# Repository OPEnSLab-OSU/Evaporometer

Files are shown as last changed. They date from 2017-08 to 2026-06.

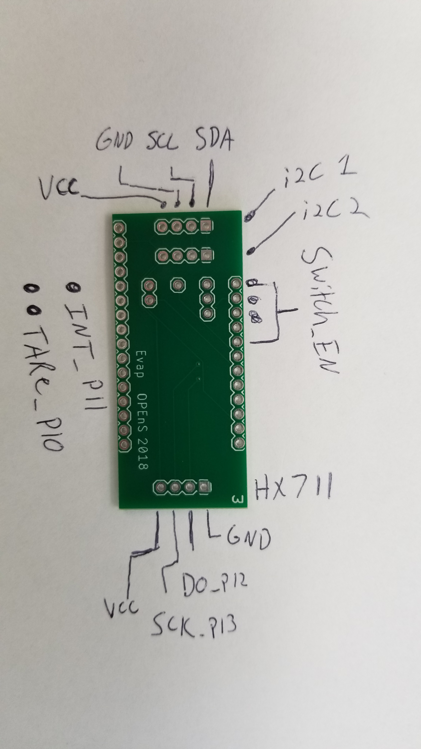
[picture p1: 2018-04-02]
PCB/20180402_102329.jpg

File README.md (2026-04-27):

# OPEnS Lab Evaporometer

Here are documented all of the files and links regarding the evapor0meter. This includes all of code and CAD files to create and program the entire system. It also includes a link to the lastest data collected in the field. 

For an overview of the project view the [Evaporometer Wiki](https://github.com/OPEnSLab-OSU/OPEnS-Lab-Home/wiki/Evaporometer)

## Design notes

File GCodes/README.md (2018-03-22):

This folder contains some important GCodes genereated for the Fusion3 F-400 printer using Simplify3D slicer program.

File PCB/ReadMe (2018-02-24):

Place to store archived EagleCAD PCB projects. Files shoudl have last data modified and version number in the name.

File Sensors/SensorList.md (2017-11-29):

These are the sensors that are on the Evaporimeter: 

[SHT31-D](https://www.adafruit.com/product/2857)  

[Load Cell](https://www.amazon.com/uxcell-Electronic-Balance-Weighing-Sensor/dp/B006W2IDUO/ref=sr_1_1?s=home-garden&rps=1&ie=UTF8&qid=1494279830&sr=1-1&keywords=load+sensor+2kg&refinements=p_85:2470955011)

[Light Sensor](https://www.adafruit.com/product/1980)

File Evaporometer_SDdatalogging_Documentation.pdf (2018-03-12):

Evaporometer PCB Pin Configuration

Feather 32u4 | P13 | P12 | P11 | P10 | P7 | P6 | P5 | SCL | SDA
Connection | HX711_ SCK (load cell) | HX711 _D0 (load cell) | DS3231_S WQ/INT (RTC) | Tare_ button | [reserved for battery input read voltage] | [open] | [open] | All SCL signals | All SDA signals

MicroSD card breakout board + (External data storage)
- Takes both 3V and 5V power source, has an onboard voltage regulator to shift 5V down to 3V.
- Keep wires short, avoid using resistor dividers for the 3.3V logic lines.
- Interface: SPI Mode “lower speed”, use this, requires four pins
- Format using FAT16 or FAT32 filesystem
- Require a lot of data transfer, best performance when connected up to the hardware SPI pins on a microcontroller.
- Use the Arduino IDE's SD library which supports FAT and FAT32 SD cards

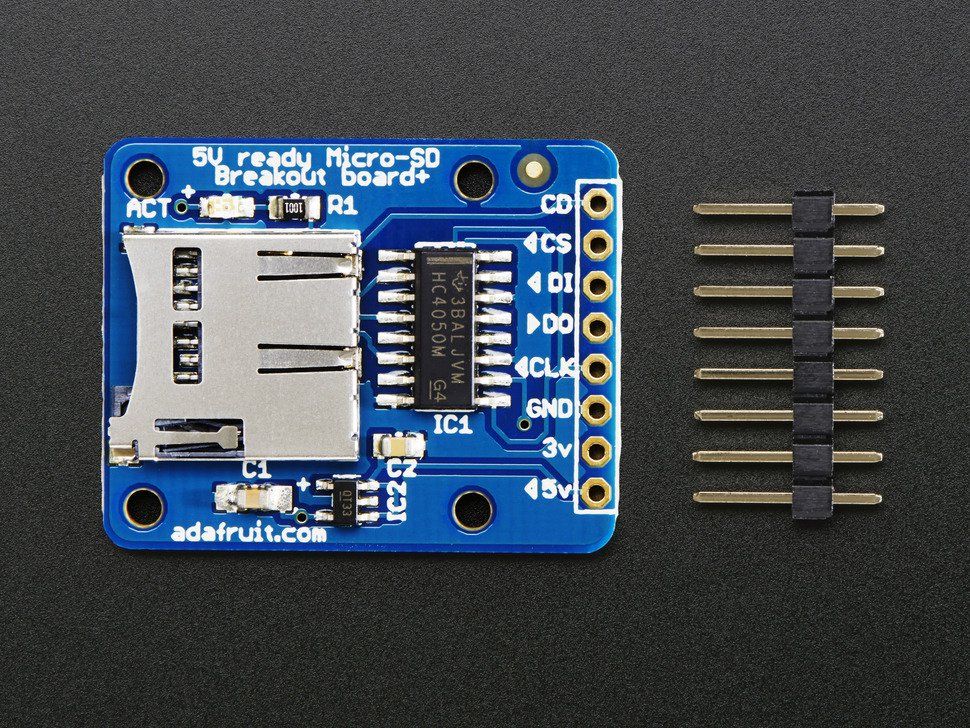
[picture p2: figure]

CD (Card Detect Pin) = Shorts to ground when a card is inserted. Connect a pull up resistor (10K or so) and wire this to another pin if you want to detect when a card is inserted.

(to Feather 32u4, NOT | shown)
CS | to #9
DI to MOSI
DO to MISO
CLK to pin SCK
GND to GND
5V to 3V

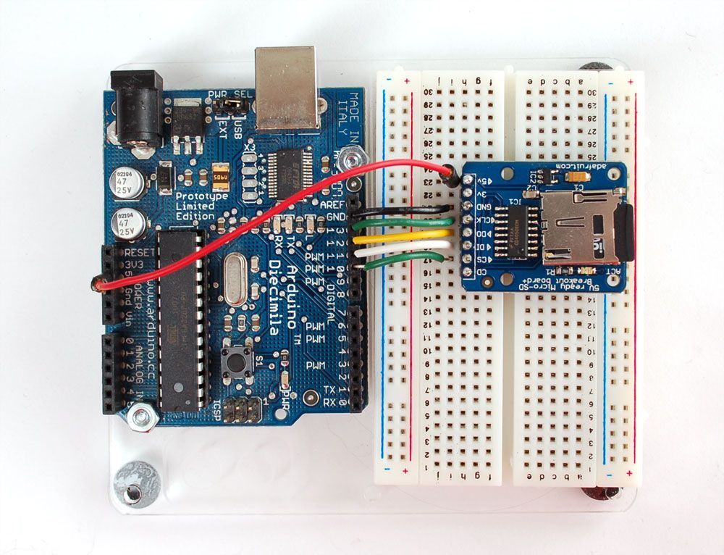
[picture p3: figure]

**the MicroSD is typically only used for the Evaporometer Hub, but included in case this is used on the Evaporometer itself**
**the Evaporometer PCB does not currently include connections for the SD card breakout, so would need to be manually connected to the Feather 32u4**
Resources: https://www.adafruit.com/product/254

Adafruit TSL2591 High Dynamic Range Digital Light Sensor
- Digital light sensor (use four outside pins)
- 12C sensor - uses the two I2C data/clock wires available on

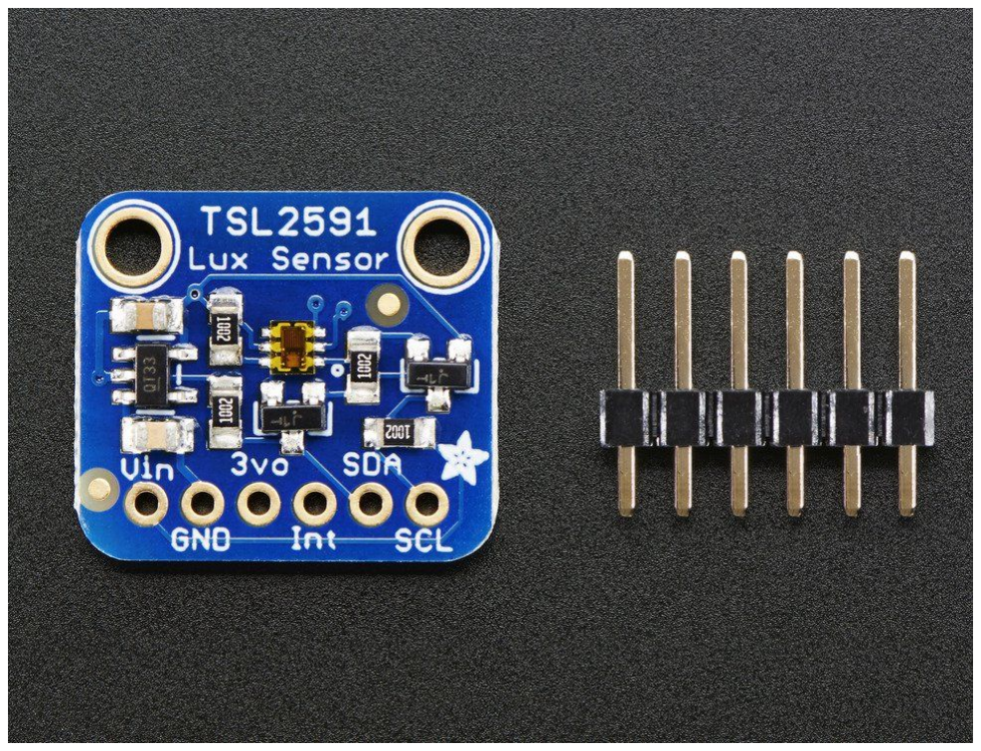
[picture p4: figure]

most microcontrollers, can share those pins with other sensors | as
long as they don't have an address collision. The I2C address is
0x29.
- Can use with any microcontroller

Vin - Power pin. The chip uses 3 VDC, a voltage regulator can take 3-5V and safely down. To power the board, give it the same power as the logic level of your microcontroller - e.g. for a 5V micro like Arduino, use 5V
3vo - The 3.3V output from the voltage regulator, can take up to 100mA from this.
GND - common ground for power and logic
SCL - I2C clock pin, connect to your microcontrollers I2C clock line.
SDA - I2C data pin, connect to your microcontrollers I2C data line.
INT - INTerrupt pin from the sensor. Can be programmed to do a couple different things with the i2c registers. For example trigger when a conversion is done, or when the light level has changed a lot.

(to Uno, shown)
Vin | to 5V
GND | to GND
SDA | to A4
SCL | to A5

(to Feather 32u4, NOT shown)
Vin | to 3V
GND | to GND
SDA | to SDA
SCL | to SCL

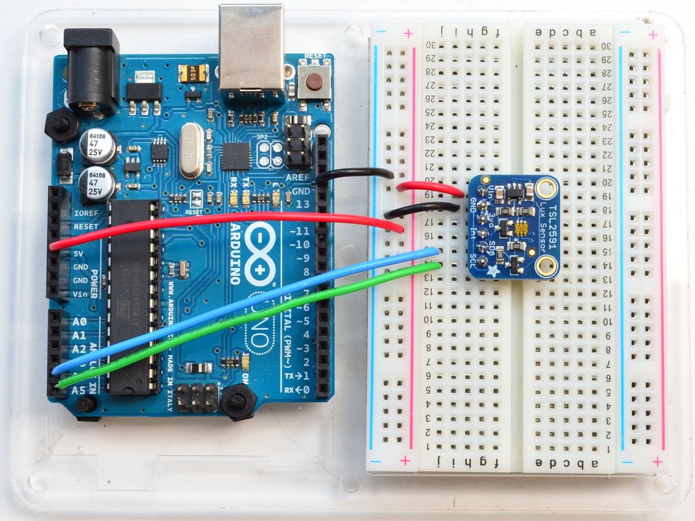
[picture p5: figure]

Resources: https://www.adafruit.com/product/1980

Adafruit Feather 32u4 RFM95 LoRa (Long Range) Radio
- 8 MHz and 3.3V logic
- 32k of flash, 2k of RAM

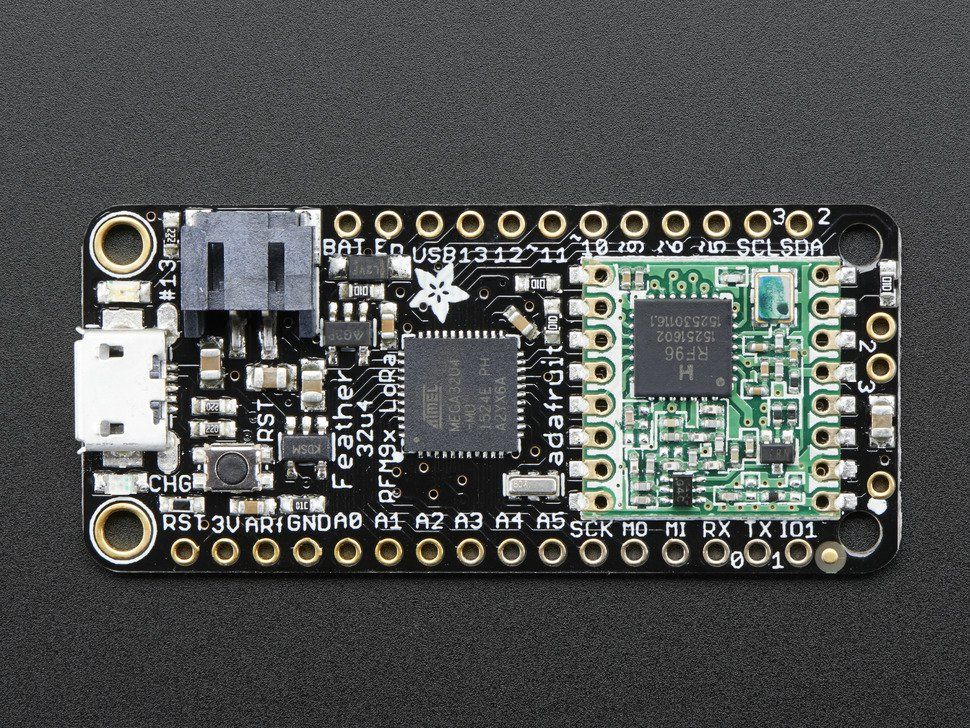
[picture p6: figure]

Power Pins
- GND - to ground
- BAT - positive voltage to/from the JST jack for the optional battery
- USB - positive voltage to/from the USB jack if connected
- EN - 3.3V regulator's enable pin. Pulled up, so connect to ground to disable the 3.3V regulator
- 3V - output from the 3.3V regulator, can supply 500mA peak
Logic Pins
- #0 / RX - GPIO #0, also receive (input) pin for Serial1 and Interrupt #2
- #1 / TX - GPIO #1, also transmit (output) pin for Serial1 and Interrupt #3
- #2 / SDA - GPIO #2, also the I2C (Wire) data pin. No pull up on this pin by default, when using with I2C, you may need a 2.2K-10K pullup. Also Interrupt #1
- #3 / SCL - GPIO #3, also the I2C (Wire) clock pin. No pull up on this pin by default, when using with I2C, you may need a 2.2K-10K pullup. Can also do PWM output and act as Interrupt #0.
- #5 - GPIO #5, can also do PWM output
- #6 - GPIO #6, can also do PWM output and analog input A7
- #9 - GPIO #9, also analog input A9 and can do PWM output. This analog input is connected to a voltage divider for the lipoly battery so be aware that this pin naturally 'sits' at around 2VDC due to the resistor divider
- #10 - GPIO #10, also analog input A10 and can do PWM output.
- #11 - GPIO #11, can do PWM output.
- #12 - GPIO #12, also analog input A11 and can do PWM output.
- #13 - GPIO #13, can do PWM output and is connected to the red LED next to the USB jack
- A0 thru A5 - These are each analog input as well as digital I/O pins.
- SCK/MOSI/MISO - These are the hardware SPI pins, used by the RFM radio module. Should be kept free as they should be available for the radio module. Also used to reprogram the chip with an AVR programmer if you need.
Radio Pins
- #8 - used as the radio CS (chip select) pin
- #7 - used as the radio GPIO0 / IRQ (interrupt request) pin.
- #4 - used as the radio Reset pin
Other

- RST - Reset pin, tie to ground to manually reset the AVR or launch the bootloader manually
- ARef - Analog reference pin. Normally the reference voltage is the same as the chip logic voltage (3.3V) but if you need an alternative analog reference, connect it to this pin and select the external AREF in your firmware. Can't go higher than 3.3V!

Resources: https://www.adafruit.com/product/3078

XFW-HX711 Load Cell (0 - 5 kg)
- 24 high-precision A/D converter, two analog input channels
- Operation supply voltage range 4.8 ~ 5.5V

(to Load Cell)
E+ | Excitation+ or VCC
E- | Excitation- or ground
A- Amplifier-A+ Amplifier+

(to Uno, shown)
VCC to 5V
GND to GND
SCK to D5
DT to D6

(to Feather 32u4, NOT shown) VCC to 3V
GND to GND
SCK to #13
DT to #12

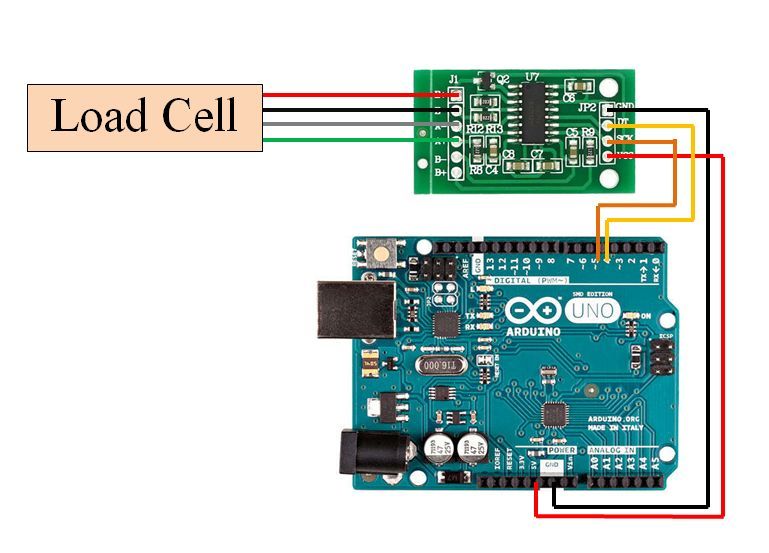
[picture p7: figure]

Resources: https://circuits4you.com/2016/11/25/hx711-arduino-load-cell/

Adafruit Sensiron SHT31-D Temperature & Humidity Sensor Breakout
- Two I2C data/clock wires can share those pins with other sensors. Default I2C address is 0x44.

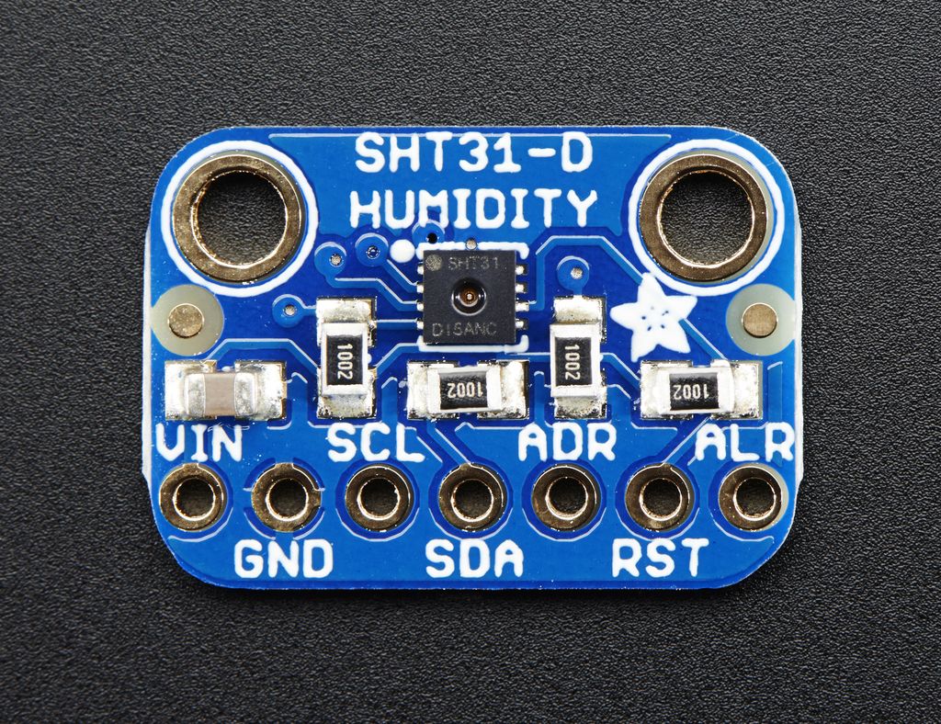
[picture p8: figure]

VIN - Power pin, can use 2.5-5VDC for power. Give it the same power as the logic level of your microcontroller - e.g. for a 5V micro like Arduino, use 5V. For a 3.3V controller like a Raspbery Pi, connect to 3.3V
GND | - Ground for power and logic.
SCL | - I2C clock pin, connect to your microcontrollers I2C clock
line. This pin has a 10K pullup resistor to Vin.
SDA - I2C data pin, connect to your microcontrollers I2C data line. This pin has a 10K pullup resistor to Vin

ADR - The I2C address selection pin. This pin has a 10K pull down resistor to make the default I2C address 0x44.
RST - Hardware reset pint. Has a 10K pullup on it to make the chip active by default. Connect to ground to do a hardware reset.
ALR - Alert/Interrupt output. Can alert when an event has occurred.

(to Metro, shown)
VIN | to 5V
GND | to GND
SCL | to SCL
SDA | to SDA
(to Feather 32u4, NOT | shown)
VIN | to 3V
GND | to GND
SCL | to SCL
SDA | to SDA

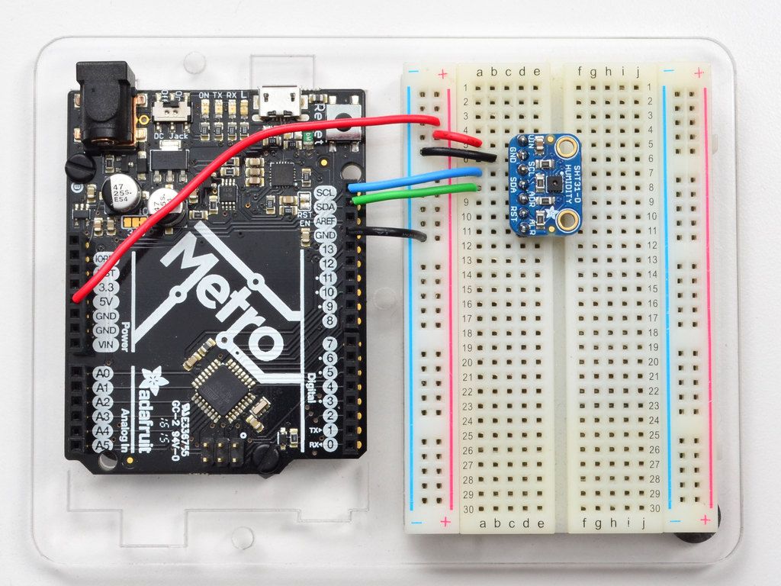
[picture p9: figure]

Resources: https://www.adafruit.com/product/2857

DS3231 Precision Real Time Clock (RTC) FeatherWing

- Internal 32kHz timing crystal with temperature sensor that compensates for frequency changes
- Easily connects to Feather boards
- Needs a CR1220 coin cell to use battery-backup capabilities

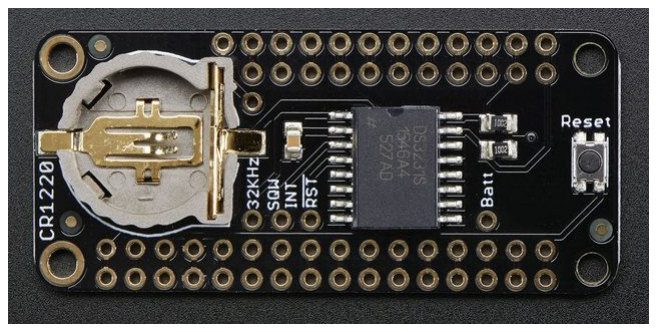
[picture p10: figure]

- SCL - I2C clock pin, connect to your microcontrollers I2C clock line. This pin has a 10K pullup resistor to 3.3V
- SDA - I2C data pin, connect to your microcontrollers I2C data line. This pin has a 10K pullup resistor to 3.3V
- BATT | - To use the battery for powering something else connect to the BATT | breakout
- 32K | - 32KHz oscillator output. Open drain, need to attach a pullup to read this signal
from a microcontroller pin (or use a microcontroller that can turn on it's internal pullup)
- SQW - Optional square wave or interrupt output. Open drain, need to attach a pullup to read this signal from a microcontroller pin (or use a microcontroller that can turn on it's internal pullup) (**signal goes to Feather Digital Pin 11 through the Evap Shield**)

- RST - Used to reset an external device or indicate when main power is lost. Open drain, but has an internal 50K pullup. The pullup keeps this pin voltage high as long as Vin is present. When Vin drops and the chip switches to battery backup, the pin goes low.

(to Feather 32u4)
The FeatherWing directly stacks on to the Feather 32u4, just make sure all the pins are correctly lined up.
**The interrupt pin on the PCB goes to P11 on the Feather 32u4**
**Only the SQW (interrupt) signal needs to be directly wired from the SQW pin on the RTC PCB to the RTC INT pin on the OPEnS lab custom Evap Shield**

Resources:
https://learn.adafruit.com/ds3231-precision-rtc-featherwing/pinoutshttps://open-sensing.squarespace.com/lorablog/2017/10/23/low-power-rtc-and-sleeping-processors-a-guided-walkthrough

Tare Button
Taring occurs in the initial setup under the load cell calibration section. The scale.tare() function resets the the scale to zero at the start of the code, so when the evaporometer is collecting load cell values from precipitation it does not take into account the weight of the container or the fibers. Will add a tare button in the future. (or can be done remotely?)
- P10 on PCB board

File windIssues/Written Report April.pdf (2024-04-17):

Evaporometer Project
Written Report
April 7, 2023
Marat Muzaffarov

I started by gathering wind data from Hydromet/Agrimet Data access. The reason why I chose their data depository is because after doing some of my own research and checking wind data across all of Corvallis, I realized that the values for the wind speed (mph) were very similar and did not change much across the entire city of Corvallis. Additionally, Hydromet had mph values per day rather than daily air movement that Hyslup had.

I also worked on creating standard deviation code and made sure that it was accurate. As we discussed, the standard deviation is based on the changes in total weight of the water, so the more it changes, the more deviation there is. I was not sure what sort of graphing method would be preferred, so if I can make any edits, please let me know. Otherwise here is the labeling:

Blue- Rain
Red- Evaporation
Yellow- Standard Deviation Value
Green- Wind speed (over the course of a day)

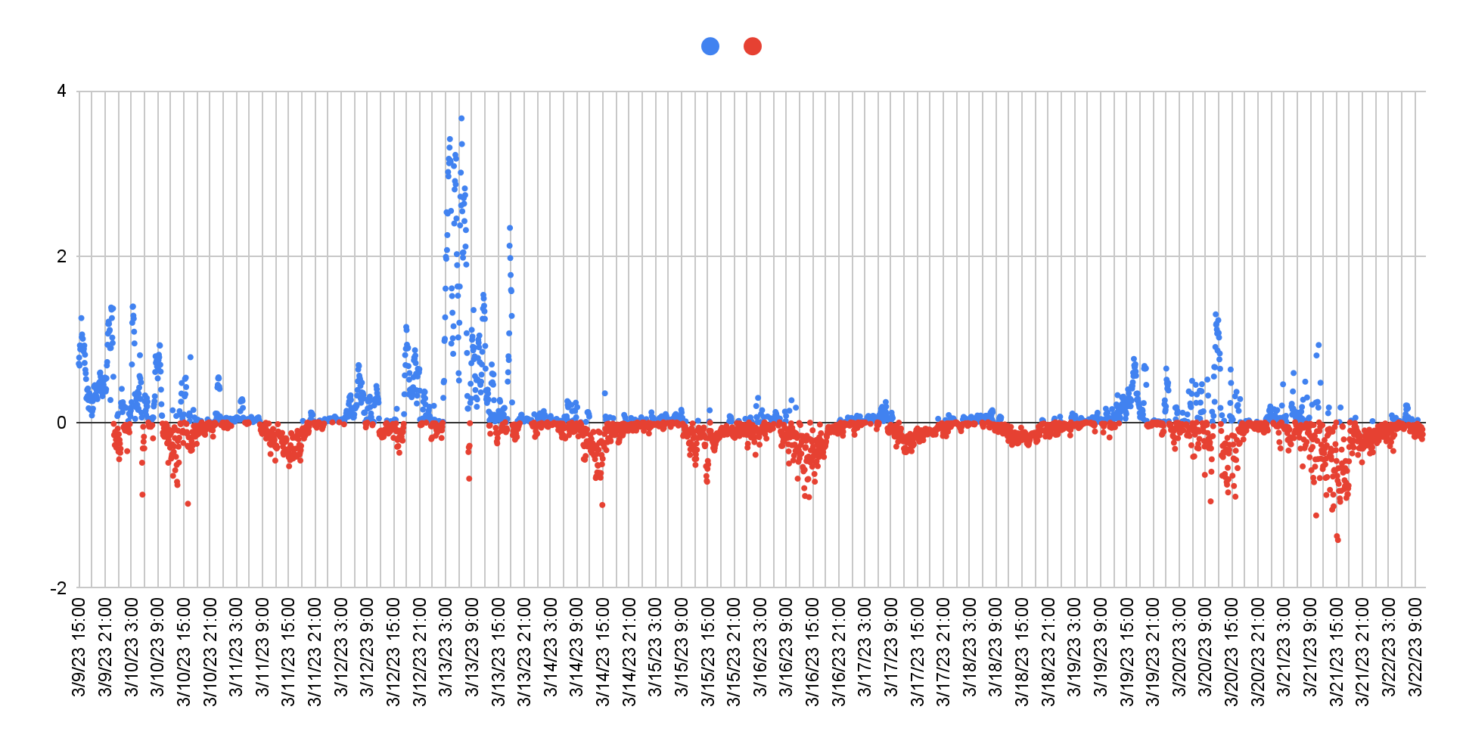
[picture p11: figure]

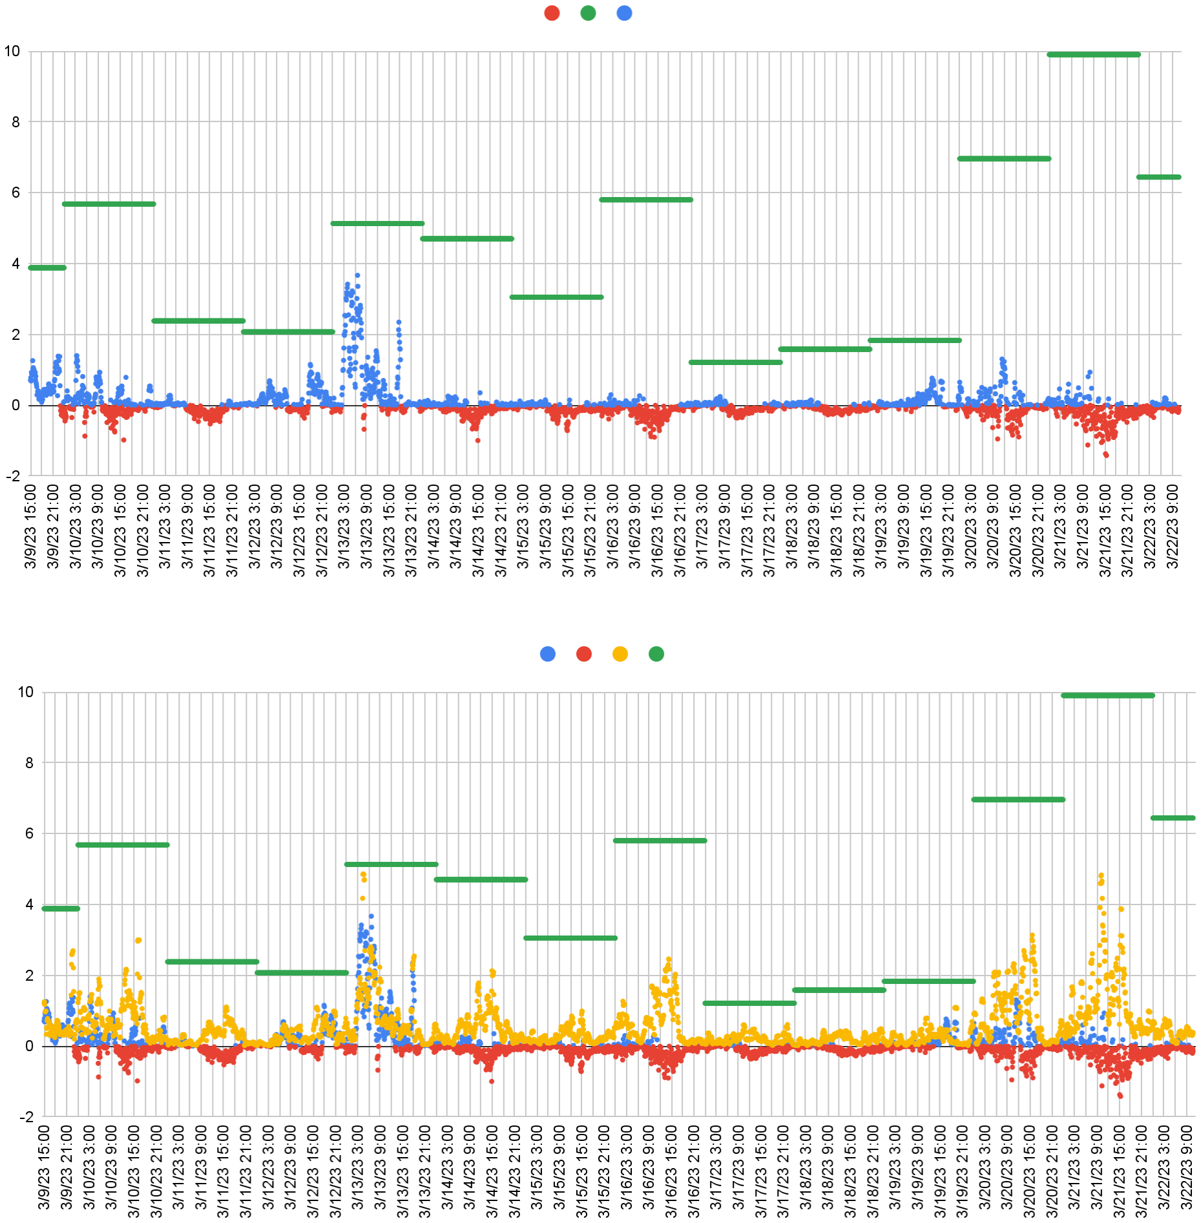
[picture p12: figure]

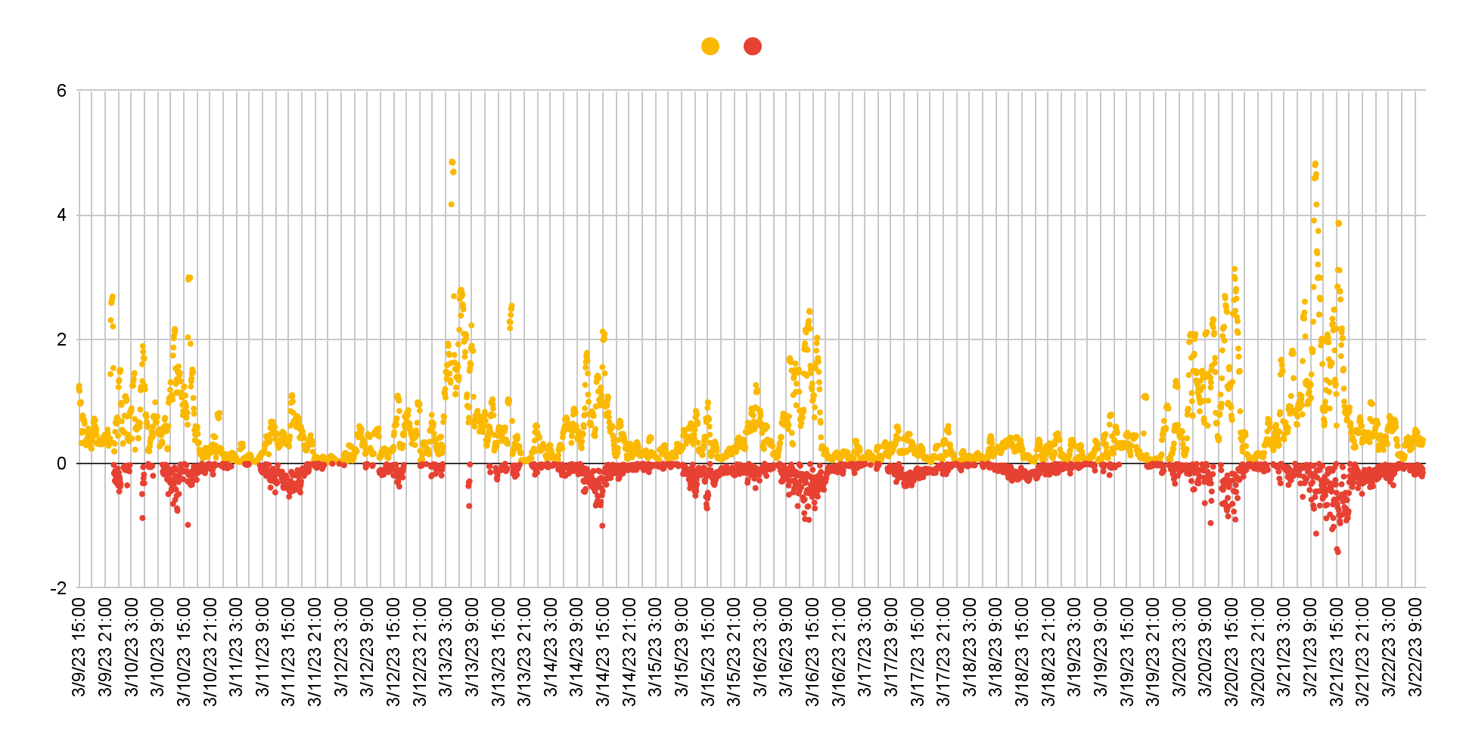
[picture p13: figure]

Based on these graphs, I do believe that there is a relationship between wind speed and the weird, unnatural rain and evaporation levels. I believe this should be looked into more, however, I will make sure to check any new data and our previous data as well, with new wind speeds.

In my upcoming report, I will run the older, December/January data through this same process and graph them as well, to see if there are any other relationships we will see.

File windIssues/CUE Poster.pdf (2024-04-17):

College of Engineering | Department of Biological and Ecological Engineering and Department of Electrical Engineering and Computer Science

# EVAPOROMETER: RAIN AND EVAPORATION DATA ANALYSIS

# Marat Muzaffarov working under Professor Selker and Gurpreet Singh in the OPEnS Lab

## Fig 1

## Fig 2

Fig 3 | Fig 4
Fig 5 | Fig 6
Fig 7 | Fig 8
Fig 9 | Fig 10

# Abstract

# Background

# Methodology and Results

# Discussion

# Acknowledgements

The Evaporometer is a device that uses a scale to measure rainfall and evaporation. Every 5

minutes, it takes dozens of weight measurements and summarizes them in a CSV file. This

poster will summarize the process of taking the raw data from the device and analyzing it to

gain information about the device and if it was working correctly. The process involved:

●Calculating rainfall, evaporation, siphoning, and the cumulative values for them.

●Graphing the calculations to learn more about how the device interacts with precipitation.

●Solving issues and fluctuations with the data by using different data analysis techniques and

data treatment methods.

●Comparing the measurements and data with wind speeds and a rolling standard deviation.

●Summarizing the findings and figuring out how to move forward.

The Evaporometer is crucial to the study of climate and will revolutionize how we measure

rainfall and especially evaporation. Currently, our measurements for evaporation at weather

stations are a crude method where a pan is filled with water and then left out to see how

much will evaporate after a few hours. Instead, the Evaporometer is able to take hundreds of

measurements every few minutes, without human intervention, allowing for real-time accurate

measurements on whether the water inside of its bucket lessened or greatened. It is also a

much cheaper device than others of its type, allowing for a wider spread of usage. By creating

this new method to measure evaporation, the Evaporometer will change what we understand

of our climate.

I would like to give a special thanks to The Office of

Undergraduate Research, Scholarship, & the Arts, funded

by the Office of Academic Affairs, and thank the College of

Enginnering for their generous contributions.

I would also like to thank Professor Selker, Gurpreet

Singh, and the rest of the team in the OPEnS Lab for

giving me this incredible learning opportunity and for

taking me on as a research assistant.

Finally, I would like to thank Hydromet for their free and

open access to weather data across the U.S.

Initially, I had to create an algorithm to calculate rainfall and evaporation. This algorithm would

read a CSV file of data from the Evaporometer, which would be weight measurements in grams

every 5 minutes, and calculate the difference between minute x and minute x+5. Once this

difference was calculated, it would divide by 5, giving the grams per minute and outputting this

information in a CSV format, for easy spreadsheet transferring. The algorithm also handles

siphoning, where the device rapidly loses weight, trying to empty itself a bit, and it recognizes

siphoning versus evaporation by setting a limit of -10 grams for evaporation, with anything

larger than that being categorized as siphoning and ignored from any calculations.

This output was used to create graphs (Figures 1 and 2) that the research group then analyzed.

There are a lot of fluctuations in the graphs, as well as rainfall and evaporation rates that

should not be possible, such as an evaporation rate of -9 grams in just 5 minutes (Figure 2). To

try and smooth the data out and get rid of outliers, I implemented median filtering (Figures 3

and 4). I editing the algorithm to assign the median of every 3 data points as the value for 15

minute intervals. I did this by creating a double for loop that correctly indexes and find the

median of every three data points from the Evaporometer. By doing this, we got a massive

improvement in spread, with the highest evaporation rate now just being slightly higher that -2

grams per 5 minutes (Figure 4), but we still had massive outliers, such as a rainfall of 6 grams

in just 5 minutes (Figure 4). Due to this, we decided to change our data treatment method to

the box-car method, which is a rolling mean. I changed the algorithm again so that for 7 data

points, it takes the average and assigns this average to the 4th, time interval, then it moves

one data point to the right and does the same thing with this new group of 7 data points. To do

this, I using a single for loop, improving the time complexity of the algorithm. I would have a

variable count up to 7 and track the position of a 2D array storing the data, while doing the

box-car method every 7 data points. This rolling mean applied over 35 minute intervals, created

a much smoother graph (Figure 5) and much better results, with the highest evaporation being

a bit higher than -1.5 grams in 5 minutes and the highest rainfall being a bit higher than 4

grams in 5 minutes (Figure 6). We decided to stick with the box-car methods for future

algorithms and instead change the algorithm to figure out what was wrong with the device or

its environment.

## Fig 7

We believed the fluctuations to be caused by wind speed, so

I added a part int he algorithm that would calculate rolling

standard deviation and daily wind speeds to new data we

receive for the month of March. To calculate the rolling

standard deviation, I would use the mean from the box-car

method to calculate the standard deviation and then assign

this value to a cell of an array. For daily wind speed, I used

another data file from USBR Pacific Northwest Region

Hydromet/AgriMet Data Access and had the algorithm read

this file and assign these values into the array.

I changed the algorithm to account for this data and then

graphed it (Figures 7, 8, 9, and 10). We found the days with

the highest rainfall and evaporation (Figure 7), also had a

higher standard deviation (Figure 9) and was associated

with higher wind speeds (Figure 8). We also found that

when we graphed everything together, we saw a correlation

between standard deviation, wind-speed, and higher peaks

in our rainfall and evaporation, pointing to wind speed being

the culprit (Figure 10).

In the future, we will attempt to both solve the issue with

the device and continue to tweak the code to adapt to the

wind issue. We hope to create a sustainable and inexpensive

device that will be able to be placed in weather stations

across the globe and give humanity a better understanding

of our climate and precipitation.

### - Rainfall

### - Evaporation

### - Standard Deviation

### - Wind Speed

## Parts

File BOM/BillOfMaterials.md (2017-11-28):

Here are located the links to the bill of materials for both the printing and electronics.

[3D Printed Parts](https://drive.google.com/drive/folders/0B7pSeRCwoKiGR2gySEM2WnBUY28) 

[Electronics](https://docs.google.com/spreadsheets/d/1A6rqY4V6Ms-nzDdnGOVL3wR1WWGpal547zaS5uAE1ZA/edit#gid=0)

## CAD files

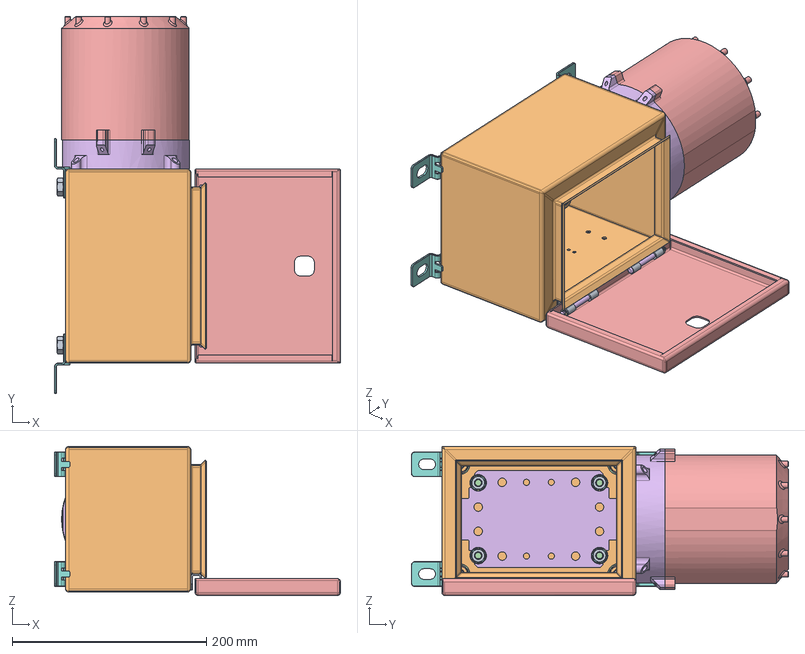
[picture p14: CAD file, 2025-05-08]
CAD/4001 R2.step
294.8 x 388.4 x 153.7 mm
SB-xxB_SB-38B-02
SB-xxC_SB-38C-02
SB-xxL_SB-01L-01
SB-PIN-01 x 2
e-ring external retaining ring_am_SB-RR-01 x 2
SB-01F-01 x 4
hex cap screw_am_SCREWS-040 x 4
hex nut style 1_am_N-003 x 4
W-005 x 4
finished circular plain washer_jis_W-006 x 4
spring lock washer_2_jis_W-007 x 4
SB-xxP_SB-38P
finished circular plain washer_jis_W-008 x 4
spring lock washer_2_jis_W-009 x 4
hex nut style 1_am_N-004 x 4
SB-HP-01 x 4

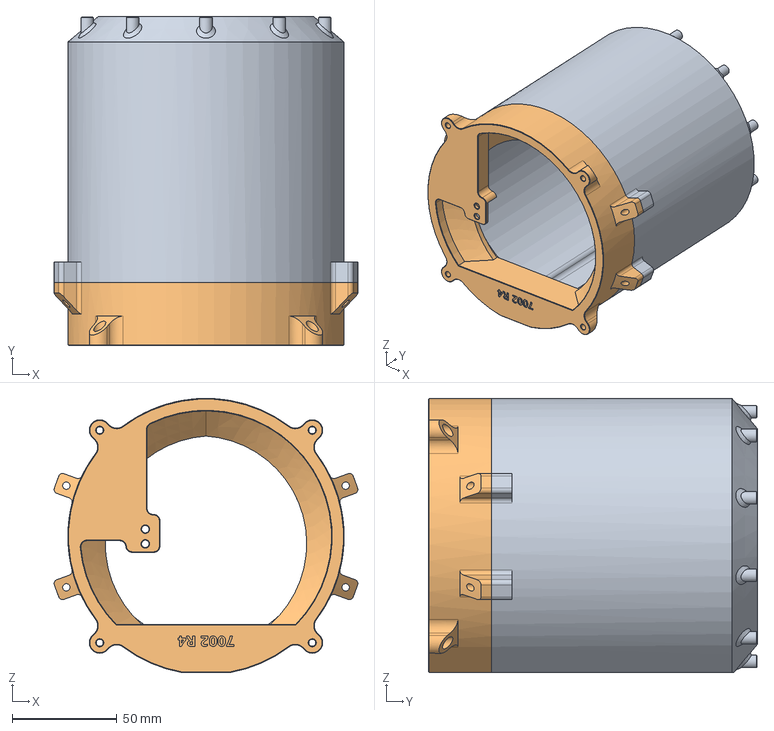
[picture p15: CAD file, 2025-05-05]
CAD/7000/7002 R4.step
145.1 x 157.2 x 131.0 mm

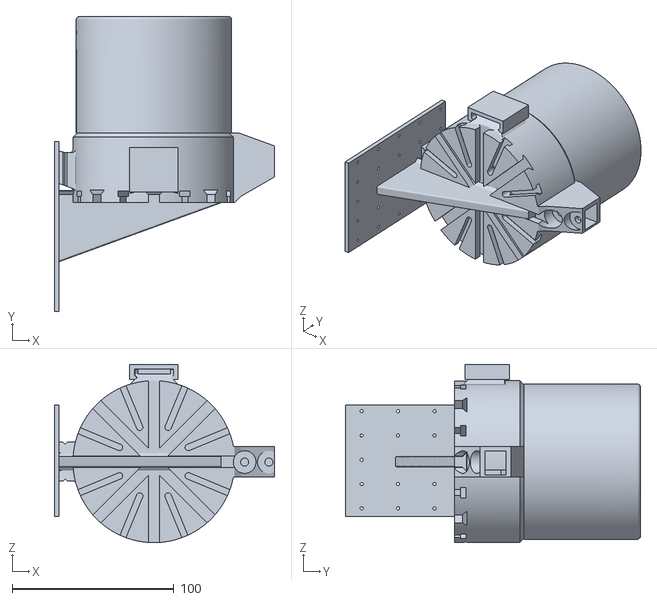
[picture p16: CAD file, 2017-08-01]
CAD/EvapModel v18.stl
136.1 x 182.2 x 110.1

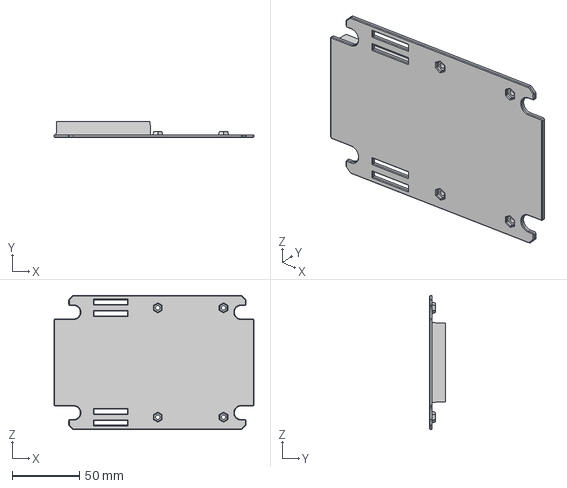
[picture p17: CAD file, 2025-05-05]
CAD/7000/7005 R1.step
149.2 x 12.0 x 100.0 mm

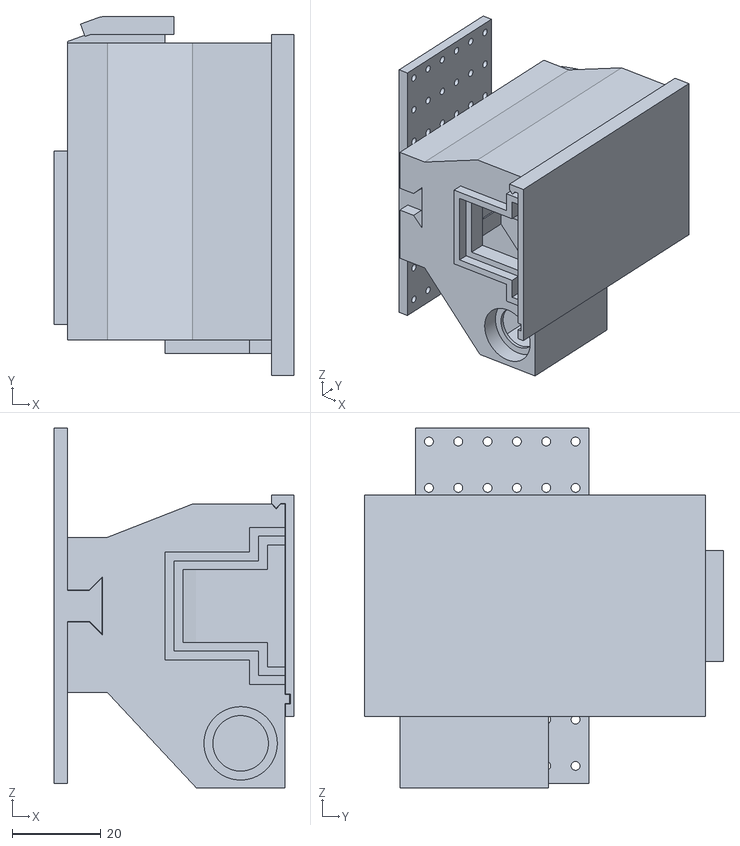
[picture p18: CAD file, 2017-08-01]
CAD/ReceiverModel.stl
54.0 x 80.8 x 80.9

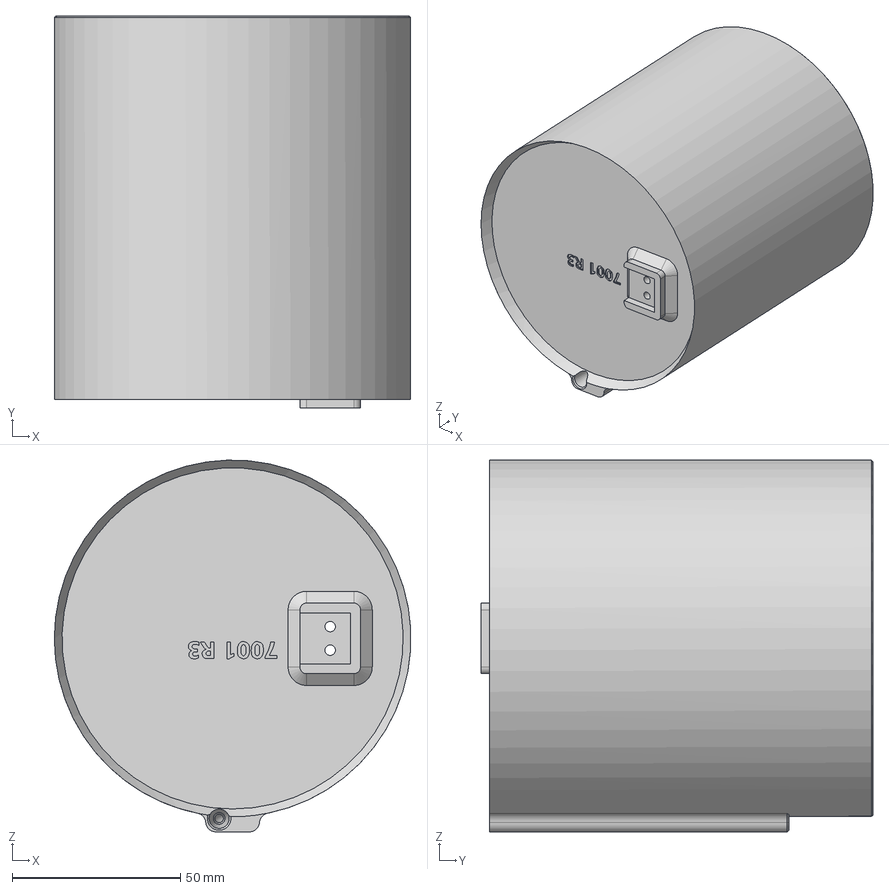
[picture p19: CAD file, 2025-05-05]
CAD/7000/7001 R3.step
105.9 x 116.5 x 110.5 mm

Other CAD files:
CAD/7000/7007 R2.step

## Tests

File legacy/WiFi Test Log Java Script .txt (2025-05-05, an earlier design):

This needs to be applied using the script editor tool within google spreadsheets in order to function. 

Specifics on how to set this up can be found here. https://www.hackster.io/detox/transmit-esp8266-data-to-google-sheets-8fc617

Code:
//-----------------------------------------------
//Originally published by Mogsdad@Stackoverflow
//Modified for The OPEnS Lab
//Modified by Thomas DeBell
//-----------------------------------------------
/*

GET request query:

https://script.google.com/macros/s/<gscript id>/exec?celData=data_here
----------------------------------------------------------------------

GScript, PushingBox and Arduino/ESP8266 Variables in order:

Variables for Evaporameter in order (Ethernet Shield) *Important Note* Variable name must match exactly to Ethenet sketch

IDtag
TimeStamp
TempC
Humid
LoadCell
IRLight
FullLight
BatVolt

----------------------------------------------------
*/

/* Using spreadsheet API */

function doGet(e) { 
  Logger.log( JSON.stringify(e) );  // view parameters

  var result = 'Ok'; // assume success

  if (e.parameter == undefined) {
    result = 'No Parameters';
  }
  else {
    var id = '1GBV7n5VxR_GrZbz92TAMLo0iQUdiJlx7OLBuS5_CrPE';//specific to the spreadsheet you are working on. this is id is found     //directly after "docs.google.com/spreadsheetURL/d" in the URL. 
   
   var sheet = SpreadsheetApp.openById(id).getActiveSheet();
    var newRow = sheet.getLastRow() + 1;
    var rowData = [];
    //var waktu = new Date();
    rowData[0] = new Date(); // Timestamp in column A
    
    for (var param in e.parameter) {
      Logger.log('In for loop, param='+param);
      var value = stripQuotes(e.parameter[param]);
      //Logger.log(param + ':' + e.parameter[param]);
      switch (param) {
        case 'IDtag': //Parameter
          rowData[1] = value; //Value in column B
          break;
        case 'TimeStamp':
          rowData[2] = value;
          break;
        case 'TempC':
          rowData[3] = value;
          break;
        case 'Humid':
          rowData[4] = value;
          break;
        case 'LoadCell':
          rowData[5] = value;
          break;
          case 'IRLight':
          rowData[6] = value;
          break;
          case 'FullLight':
          rowData[7] = value;
          break;
          case 'BatVolt':
          rowData[8] = value;
          break;
        default:
          result = "unsupported parameter";
      }
    }
    Logger.log(JSON.stringify(rowData));

    // Write new row below
    var newRange = sheet.getRange(newRow, 1, 1, rowData.length);
    newRange.setValues([rowData]);
  }

  // Return result of operation
  return ContentService.createTextOutput(result);
}

/**
* Remove leading and trailing single or double quotes
*/
function stripQuotes( value ) {
  return value.replace(/^["']|['"]$/g, "");
}

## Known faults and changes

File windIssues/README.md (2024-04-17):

In the early developments of a script to analyze the Evaporometer data, we came across issues where the data had high amounts of noise and irregular activity. 

After closer examination, our team found that the Evaporometer had spikes in noise and values whenever wind speeds were the highest.

This directory stores the documentation and process for discovering this relationship.

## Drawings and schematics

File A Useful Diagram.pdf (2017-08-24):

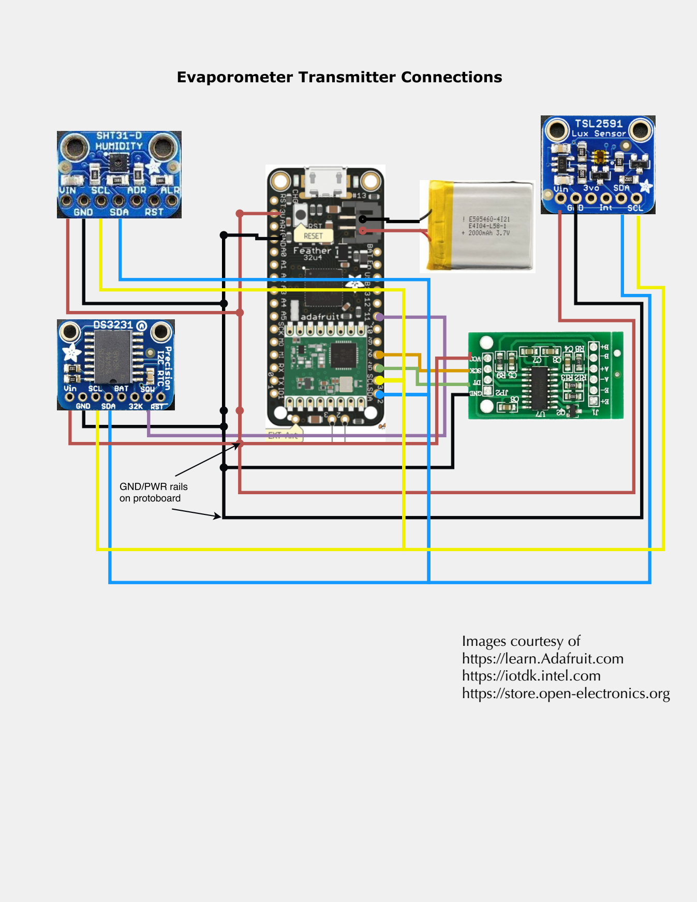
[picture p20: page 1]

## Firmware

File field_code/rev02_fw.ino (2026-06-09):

/*
 * Title: Evaporometer Rev 02
 * Author: Evan Hockert
 */

#include <Loom_Manager.h>
#include <ADS1232_Lib.h>
#include <Hardware/Loom_Hypnos/Loom_Hypnos.h>
#include <Hardware/Loom_Hypnos/SDManager.h>
#include <algorithm>

#define ADC_SEL A1
#define DOUT A3
#define SCLK A4
#define PDWN A5
#define VREFEN MOSI

#define VBATPIN A7
#define SDI_EN

#define LOADCELL_CHANNEL 0
#define THERMISTOR_CHANNEL 1

#define MAX_24_BITS 16777215
#define MAX_23_BITS 8388607

// Set calibration params here
#define OFFSET 8402647
#define SCALE 0.032

// 8423296
// 8429402

/*
 * for a calibration weight of size C measured with an 
 * ADC raw output of counts, we have that
 * SCALE = C / (counts - offset)
 */

//#define OFFSET 0
//#define SCALE 1
/*
 * 3/8/2026: 
 * offset 8422422
 * scale 0.0315
 */

// use only raw values
#define CALIBRATION_MODE 1

// Set how many times the ADC Reads. Nominal 50
#define NUM_ADC_READS 40

// Use SD card or sleeping
#define LOGGING_MODE 0

// Output to Serial Monitor Graph
#define DEMO_MODE 0

Manager     manager("Device", 1);
ADS1232_Lib ads(PDWN, SCLK, DOUT);
Loom_Hypnos hypnos(manager, HYPNOS_VERSION::V3_3, TIME_ZONE::PST, true, true);
SDManager   sd(&manager, 11);

const float resistanceLUT[] = {
  32739.8, 31109.2, 29569.5, 28115.0,
  26740.6, 25441.4, 24212.9, 23050.9,
  21951.4, 20910.8, 19925.5, 18992.3,
  18108.2, 17270.4, 16476.1, 15722.9,
  15008.5, 14330.6, 13687.1, 13076.3,
  12496.1, 11945.0, 11421.3, 10923.4,
  10450.1, 10000.0, 9571.77, 9164.26,
  8776.38, 8407.07, 8055.35, 7720.30,
  7401.03, 7096.72, 6806.60, 6529.94,
  6266.03, 6014.23, 5773.93, 5544.53,
  5325.50, 5116.30, 4916.46, 4725.49,
  4542.98, 4368.49, 4201.64, 4042.05,
  3898.38, 3743.29, 3603.46
};

const int LUT_SIZE = sizeof(resistanceLUT) / sizeof(resistanceLUT[0]);

long readCounts(uint8_t channel) {
  // channel = 0 -> Load Cell
  // channel = 1 -> Thermistor   
  digitalWrite(ADC_SEL, channel);
  
  /* read counts from the adc. this represents the weight
  as an integer between 0 and 2^24 - 1 */
  ads.power_up();
  
  // empty the output buffer
  ads.raw_read(10);
  long counts = ads.raw_read(NUM_ADC_READS);

  return counts;
}

float readWeight(uint8_t use_raw_counts = 0) {
  // turn on the bridge excitation
  digitalWrite(VREFEN, 1);
  manager.pause(100);
  long weight = readCounts(LOADCELL_CHANNEL);
  digitalWrite(VREFEN, 0);

  if (!use_raw_counts && !CALIBRATION_MODE) {
    float calibrated_weight = (weight - OFFSET) * SCALE;
    return calibrated_weight;
  }
  else {
    return weight;
  }
}

void printWeight() {
  float weight = readWeight();
  Serial.println("Weight: ");
  Serial.println(weight);
}

// r is resistance of thermistor. Nominally 10k
float temperatureLookUp(float r) {
  // check every adjacent pair in the LUT
  for (uint8_t i = 0; i < LUT_SIZE - 1; i++){
    // if the resistance is within a pair
    if (r <= resistanceLUT[i] && r >= resistanceLUT[i+1]) {
      // interpolate the temperature
      float numer = resistanceLUT[i] - r;
      float denom = resistanceLUT[i] - resistanceLUT[i+1];
      
      // in our LUT the index is temp in degrees C

      return i + (numer / denom);
    }
  }
  // if the input was out of range return -1
  return -1;
}

float readTemperature() {
  // turn on the bridge excitation
  digitalWrite(VREFEN, 1);
  manager.pause(100);
  // read thermistor channel
  long counts = readCounts(THERMISTOR_CHANNEL);
  digitalWrite(VREFEN, 1);
  //Serial.print("counts: ");
  //Serial.println(counts);
  
  Serial.print("counts: ");
  Serial.println(counts);

  // transform from counts to volts
  // The ads1232_lib will output 2^23 for an input of 0
  // volts and 2^24 for an input of v_ref / (2*adc_gain)
  float gain = 2;
  float v_ref = 3.01;
  
  float volts = (1 - counts / (MAX_23_BITS + 1)) * v_ref / (2 * gain);

  volts = -1 * (1 - counts / (pow(2,23))) * v_ref / (2 * gain);
  Serial.print("a: ");
  Serial.println(volts);

  Serial.print("volts: ");
  Serial.println(volts,4);
  
  //Serial.print("volts: ");
  //erial.println(volts, 12);

  // transform from volts to resistance of thermistor
  int R = 10000;
  //float denom =  (volts / 3) + 0.5; 
  //float resistance = (R / denom) - R;

  // v_sig = (R / (R + R_t) - 0.5)*v_ref
  // v_sig / v_ref + 0.5 = R /(R + R_t)
  // (v_sig / v_ref + 0.5)/R = 1/ (R + R_t)
  // R / (v_sig / v_ref + 0.5) - R = R_t

  float resistance = R / (volts / v_ref + 0.5) - R;

  Serial.print("resistance: ");
  Serial.println(resistance);
  // use the lookup table and interpolation to find temperature
  float temperature = temperatureLookUp(resistance);
  return temperature;
}

void printTemperature() {
  float temp = readTemperature();
  Serial.print("Temperature: ");
  Serial.println(temp, 8);
}

float readVbat(){
  float measuredvbat = analogRead(VBATPIN);
  measuredvbat *= 2;    // we divided by 2, so multiply back
  measuredvbat *= 3.3;  // Multiply by 3.3V, our reference voltage
  measuredvbat /= 1024; // convert to voltage
  return measuredvbat;
}

/*
 *    Function: log_date
 *    Description: Logs weight and temp to SD card
 *    Logs by default to "Device0.csv"
 *
 */
void logData(float weight, float temp, float vbat){
  //Get the current time from hypnos and save it as a c str
  char buf1[32] = {};
  DateTime now = hypnos.getCurrentTime();
  
  sprintf(buf1, "%02d:%02d:%02d %02d/%02d/%02d",  
          now.hour(), now.minute(), now.second(),
          now.day(), now.month(), now.year());
  
  char buf2[32] = {};
  sprintf(buf2, "%.2f", weight);

  char buf3[32] = {};
  sprintf(buf3, "%.2f", temp);

  char buf4[32] = {};
  sprintf(buf4, "%f", vbat);

  //Combine the time and measurments strings. Include "," to separate columns
  char date_and_data[128] = {};
  strcat(date_and_data, buf1);
  strcat(date_and_data, ",");
  strcat(date_and_data, buf2);
  strcat(date_and_data,",");
  strcat(date_and_data, buf3);
  strcat(date_and_data, ",");
  strcat(date_and_data, buf4);

  sd.writeLineToFile("Device0.csv", date_and_data);
}

void isr_Trigger(){
  hypnos.wakeup();
}

void sleep(uint8_t seconds=0, uint8_t minutes = 1) {
  digitalWrite(VREFEN, 0);
  hypnos.setInterruptDuration(TimeSpan(0, 0, 0, 30));
  hypnos.reattachRTCInterrupt();
  hypnos.sleep();
}

void setup() {
  manager.beginSerial();
  Serial.println("Starting Setup");
  
  if (LOGGING_MODE) {hypnos.enable(true, false);}
  
  manager.initialize();

  pinMode(ADC_SEL, OUTPUT);
  pinMode(VREFEN, OUTPUT);
  // ADC library setup
  ads.set_offset(0);
  ads.set_scale(1);

  // set SD card write pins
  if (LOGGING_MODE) {
    pinMode(23, OUTPUT);
    pinMode(24, OUTPUT);
    pinMode(11, OUTPUT);
    sd.begin();
    hypnos.registerInterrupt(isr_Trigger);
  }

  Serial.println("End of Setup");
}

void loop() {

  float temp = 0;
  float vbat = 0;

  float weight = readWeight();
  temp = readTemperature();
  vbat = readVbat();

  if (DEMO_MODE) {
    Serial.println(weight);
  } else {
    Serial.print("weight: ");
    Serial.println(weight); 
    Serial.print("temperature: ");
    Serial.println(temp);
  }

  if (LOGGING_MODE) {
    logData(weight, temp, vbat);
    sleep();
  }
}

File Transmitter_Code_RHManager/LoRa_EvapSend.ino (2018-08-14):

/* Authors: Chet Udell, William Selbie, Thomas DeBell
    Date: 04/26/2018
   Updated Version using RH Manager and M0 Processor
  Description: Code for "Transmitter" LoRa radio Feather Board; initilizes
  LoRa radio transmitter and sends data to LoRa receiver on the same
  frequency.

  This code originated from Adafruit's website and has been
  adjusted for use in the Internet of Agriculture project.
  Beginning Researcher student Research at OPEnS Lab at Oregon State
  University.
  // Important Example code found at https://learn.adafruit.com/adafruit-rfm69hcw-and-rfm96-rfm95-rfm98-lora-packet-padio-breakouts/rfm9x-test


*/

// LoRa 9x_TX
// -*- mode: C++ -*-
// Example sketch showing how to create a simple messaging client(transmitter)
// with the RH_RF95 class. RH_RF95 class does not provide for addressing or
// reliability, so you should only use RH_RF95 if you do not need the higher
// level messaging abilities.
// It is designed to work with the other example LoRa9x_RX

#include <SPI.h>
#include <RH_RF95.h> // Important Example code found at https://learn.adafruit.com/adafruit-rfm69hcw-and-rfm96-rfm95-rfm98-lora-packet-padio-breakouts/rfm9x-test
#include <RHReliableDatagram.h>
#include "HX711.h"  //https://learn.sparkfun.com/tutorials/load-cell-amplifier-hx711-breakout-hookup-guide
#include "LowPower.h" // from sparkfun low power library found here https://github.com/rocketscream/Low-Power
#include "RTClibExtended.h"// from sparkfun low power library found here https://github.com/FabioCuomo/FabioCuomo-DS3231/
//------------------------------------------------------------------------
// Humidity/Temperature Sensor Settings--------------------
//------------------------------------------------------------------------
//#include <Arduino.h>
#include <Wire.h>
#include "Adafruit_SHT31.h" // https://github.com/adafruit/Adafruit_SHT31
// ------------------------------------------------------------------------
// Infrared/Full Light Sensor Settings--------------------
//------------------------------------------------------------------------
#include <Adafruit_Sensor.h>
#include "Adafruit_TSL2591.h" // https://github.com/adafruit/Adafruit_TSL2591_Library
//------------------------------------------------------------------------
// Debug Mode, Set flag to 0 for normal operation
//------------------------------------------------------------------------
#define DEBUG 1
//------------------------------------------------------------------------
// LORA pins --------------------
//------------------------------------------------------------------------
#define RFM95_CS 8
#define RFM95_RST 4
#define RFM95_INT 7

#define SERVER_ADDRESS 2
//battery voltage read pin
#define VBATPIN A9

//super validator calibration variable//
#define calibration_factor 430000//This value is obtained using the Calibration sketch (grams)

//load cell variables//
#define DOUT 5 //connecting the out and clock pins for the load cell
#define CLK 6


//Global Set-up//
float temp, humidity, loadCell, measuredvbat;
String IDstring, tempString, humidityString, loadCellString, lightRString, lightGString, lightBString, lightIRString, lightFullString, vbatString, RTC_monthString, RTC_dayString, RTC_hrString, RTC_minString, RTC_timeString, stringTransmit;
int transmitBufLen; // length of transmit buffer
const int ID = 100;
uint16_t lightR, lightG, lightB, lightIR, lightFull;
//char transmitBuf[23]; // this needs to be the length of the transmission buffer
float temp_ar[5], humidity_ar[5], loadcell_ar[5];
uint16_t lightIR_ar[5], lightFull_ar[5];

HX711 scale(DOUT, CLK);

// Change to 434.0 or other frequency, must match RX's freq!
#define RF95_FREQ 915.0

// Singleton instance of the radio driver
RH_RF95 rf95(RFM95_CS, RFM95_INT);
RHReliableDatagram manager(rf95, SERVER_ADDRESS);

// Evap code from Manuel instance of temp/humidity sensor
Adafruit_SHT31 sht31 = Adafruit_SHT31();

// Create instance of TSL2591 light sensor
Adafruit_TSL2591 tsl = Adafruit_TSL2591(2591); // can pass in a number for the sensor identifier (for your use later)

// Create instance of DS3231 called RTC
RTC_DS3231 RTC; //we are using the DS3231 RTC

// declare/init RTC variables//
volatile bool TakeSampleFlag = false; // Flag is set with external Pin A0 Interrupt by RTC
volatile bool LEDState = false; // flag t toggle LED
volatile int HR = 8; // Hr of the day we want alarm to go off
volatile int MIN = 0; // Min of each hour we want alarm to go off
volatile int WakePeriodMin = 1;  // Period of time to take sample in Min, reset alarm based on this period (Bo - 5 min)
const byte wakeUpPin = 11;

////////////////////////
void setup()
{
  // convert ID into String, done up here because we only need this done once
  IDstring = String(ID, DEC);
  pinMode(wakeUpPin, INPUT_PULLUP);

  // Turns on temp and humid sensor //
  sht31.begin(0x44);
  // load cell calibration
  scale.set_scale(calibration_factor); //This value is obtained by using the Calibration sketch
  scale.tare(); //Assuming there is no weight on the scale at start up, reset the scale to 0
  scale.power_down(); // Go into low power mode

  //LoRa transmission//
  pinMode(RFM95_RST, OUTPUT);
  digitalWrite(RFM95_RST, HIGH);
  Serial.begin(9600);
  //while (!Serial); // waits for serial hardware to start up
#if DEBUG == 1
  //report all sensors present on system
  Serial.println(" LoRa Feather Transmitter Test!");
  Serial.println("HX711 scale");
  Serial.println("Starting Adafruit TSL2591 Test!");
#endif
  
  //check light sensor init
  while (!tsl.begin())
  {
  #if DEBUG == 1
    Serial.println("No sensor found ... check your wiring?");
  #endif  
    while (1);
  }
  #if DEBUG == 1
  Serial.println("Found a TSL2591 sensor");
  #endif
  /* Configure the sensor */
  configureSensor();
  //there's an option to print sensor details in example code - this requires addit'l functions and takes up too much space

  //manually reset LoRa
  digitalWrite(RFM95_RST, LOW);
  delay(10);
  digitalWrite(RFM95_RST, HIGH);
  delay(10);
  while (!manager.init()) {
    #if DEBUG == 1
      Serial.println("LoRa manager init failed"); //if print wiring may be wrong
    #endif
    while (1);
  }
  #if DEBUG == 1
    Serial.println("LoRa radio init OK!");
  #endif
  // checks if frequency is initialized
  // Defaults after init are 434.0MHz, modulation GFSK_Rb250Fd250, +13dbM
  if (!rf95.setFrequency(RF95_FREQ)) {
    #if DEBUG == 1
      Serial.println("setFrequency failed");
    #endif
    while (1);
  }
  #if DEBUG == 1
    Serial.print("Set Freq to: ");
    Serial.println(RF95_FREQ);
  #endif

  // Defaults after init are 434.0MHz, 13dBm, Bw = 125 kHz, Cr = 4/5, Sf = 128chips / symbol, CRC on
  // The default transmitter power is 13dBm, using PA_BOOST.
  // If you are using RFM95/96/97/98 modules which uses the PA_BOOST transmitter pin, then
  // you can set transmitter powers from 5 to 23 dBm:
  rf95.setTxPower(23, false);


  //RTC stuff init//

  InitalizeRTC();
  #if DEBUG == 1
    Serial.print("Alarm set to go off every "); Serial.print(WakePeriodMin); Serial.println("min from program time");
  #endif
  delay(1000);
}
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

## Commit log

2017-03-24 Create SuperValidatorCalibration
    This example is from sparkfun and we only changed the output for the units and the calibration factor that it initially had to the one that works with our 2kg strain gauge.
2017-03-24 Create SuperValidatorDisplayMass
    This example uses that code from sparkfun and the only change was the calibration factor obtained from running the calibration code for this same project
2017-08-01 Add files via upload
    Receiver Assembly
    [ReceiverModel.stl]
2017-08-01 Add files via upload
    TransmitterModel
    [EvapModel v18.stl]
2017-08-01 Add files via upload
    These are the two current scripts for the Transmitter (tx) and Receiver (TestRec)
2018-02-24 Uploaded V1 of EvapShark combo PCB
2018-03-06 Update evap_ethernet.ino
    Updates to existing code. Currently working test code.
2018-03-07 Transmitter update supports TSL2561 not TSL2591
    transitioning to light sensor version with re-addressable pins to support multiple sensors
2018-03-07 Evaporometer PCB V1
2018-04-02 Add files via upload
    Updated Diagram for Evaporometer PCB
2023-04-17 Create OnePiece board
    [Evaporometer_OnePiece.sch]
2025-05-05 Add files via upload
    Current 2024 printed models
    [7001 R3.step, 7002 R4.step, 7005 R1.step, 7007 R2.step]
